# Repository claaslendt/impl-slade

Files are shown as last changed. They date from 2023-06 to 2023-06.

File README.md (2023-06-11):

Author: Claas Lendt (I'm tweeting @claaslendt)

Last modified: 10.06.2023

*Note: This is a living documentation and will be continuously extended and reviewed.*

</br>

## A wearable system to estimate energy expenditure

My PhD research focusses on the development and validation of new computational methods to monitor human physical behaviour based on the acceleration of the thigh. One key area of my research is the estimation of activity-induced energy expenditure. In other words, I want to develop an accurate algorithm to estimate how many calories are burned when someone is physically active. To achieve this goal, I need data to develop my algorithm and see how accurate it really is. These data include a primary reference for the energy expenditure (also considered ground truth), raw triaxial acceleration of the thigh and further references from existing methods.

One particular method I want to compare my algorithm against is the wearable system proposed by Patrick Slade and colleagues (Link to the paper: [Slade et al. 2021 - Nature Communications](https://www.nature.com/articles/s41467-021-24173-x)). It comprises two inertial measurement units (IMUs) on the thigh and the shank, a Raspberry Pi as the computing unit, a rechargeable battery and a regression model. The estimation of the energy expenditure is based on a linear regression model with accelerometer and gyroscope data as inputs. Their novel approach uses stride segmentation of the IMU data and then performing the energy expenditure estimation on discrete stride cycles. This is super interesting, given that most other computational methods are based on some form of regression model with an aggregated measure of the acceleration over a fixed time interval. Overall, a highly innovative and quite accurate approach!

It seems like the wearable system from Patrick Slade et al. is a good candidate to compare my future estimations against! So I decided to recreate the system based on the information given in the paper and its supplementary documents. It's been quite a journey, given that I had almost zero knowledge on the Raspberry Pi, I2C addresses or 3D printing at the start of this project.

</br>

## Building the system (almost) from scratch

To start with, I chose a [Raspberry Pi Zero 2 W](https://www.raspberrypi.com/products/raspberry-pi-zero-2-w/) as my computing unit. It's quite compact compared to the Raspberry Pi 4 and still powerful enough to allow the collection and processing of the IMU data. Further, it can easily run Python code. I haven't used any Raspberry Pi before, but it was extremely easy to get started. There are great documentations available online (see [raspberrypi.com/documentation](https://www.raspberrypi.com/documentation/computers/getting-started.html)) and setting up the mini-computer can be done in short time.

As for the IMUs, I chose the [Adafruit ISM330DHCX](https://www.adafruit.com/product/4502) sensor breakout boards. These sensors allow to capture a range of ±16 g of acceleration and up to ±4000 dps. The breakout boards are great because they can easily be connected to a computing unit using the integrated STEMMA QT connectors. In my case, the Raspberry Pi and the IMUs are connected using 50cm [STEMMA QT](https://www.adafruit.com/product/5385) (also called "Qwiic") connection cables and a [SparkFun Qwiic SHIM adapter](https://www.adafruit.com/product/4463) for the Raspberry Pi. At the beginning, I thought I could create the system without the need for any soldering. But I was wrong. Thankfully, I got support from our electronics lab in soldering the pins to the Raspberry Pi and the adapter as well as setting the alternative I2C address for the IMU at the shank.

The final component is an 10.000mAh USB rechargeable battery to power the system during mobile use. The battery is simply connected to the Raspberry Pi using a short USB cable (USB-A to micro-USB). I went with the Ansmann PB320PD.

</br>

**Figure 1.** The Raspberry Pi Zero 2 W, the two Adafruit IMUs and the STEMMA QT/Qwiic connections using the SparkFun SHIM adapter on the Raspberry Pi.

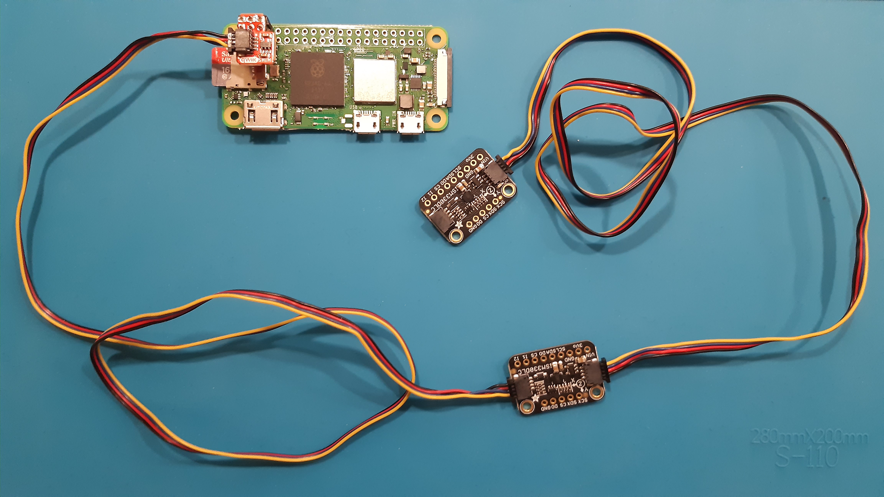
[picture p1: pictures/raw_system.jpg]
raw_system


</br>

### 3D printing the cases

The two IMUs and the Raspberry Pi need to be attached to the body and be protected from receiving any damage during movements. I decided to 3D print my own cases since there wasn't any simple solution available. My starting point was the great article [3D Printed Case for Adafruit Feather](https://learn.adafruit.com/3d-printed-case-for-adafruit-feather/3d-printing) and I iteratively developed my own version to fit the Raspberry Pi Zero and a smaller case for the IMUs. I used Autodesk Fusion 360 for the modelling of the individual parts, which required some time to learn the software. A much easier and no-cost option may be [Autodesk's Tinkercad](https://www.tinkercad.com/).

Each case consists of a base unit and a top. The connection cables can be attached through the small holes. The Raspberry Pi and the IMU boards are attached to the case using small plastic screws (M2.5) and hex nuts. I am also sharing the files used for printing within the 3d_printing folder.

</br>

**Figure 2.** The two cases for the IMUs with the screws and hex nuts fixating the IMUs to the case. The additional wings on the cases are used to attach the cases with additional elastic straps (see below).

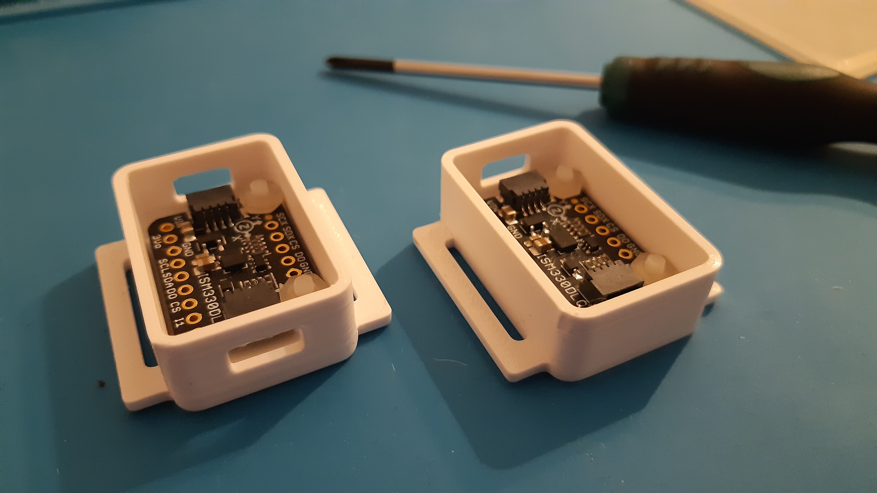
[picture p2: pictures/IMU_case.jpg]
IMU_case


</br>

### Attaching the IMUs to the leg

I did quite some experimenting with different elastic straps to attach the sensors to the thigh and shank as I wanted them to be lightweight, comfortable and not slipping too much. At the end, I found some elastic straps which are used to attach urine drainage bags (see [MedlinePlus: Medical Encyclopaedia](https://medlineplus.gov/ency/patientinstructions/000142.htm)) and they work great! The strap has a layer of silicone rubber which prevents any slippage during movements of the leg and can easily be attached using the velcro. The PZN (German Medical Product ID) for these particular straps is 08913533.

</br>

**Figure 3.** The medical straps used to attach the sensor units to the shank and thigh.

elastic_strap

</br>

## The final system - completed!

When everything is put together, the Raspberry Pi and the battery are attached to the waist using an elastic belt with a quick-release. The two IMUs are attached to the shank and thigh. The system has been quite comfortable during my piloting (walking and running on a treadmill as well as cycling on an ergometer).

</br>

**Figure 4.** The left (A) shows the complete system with the battery (lower left) connected to the Raspberry Pi (lower right) via USB. The Raspberry Pi is connected to the IMU at the thigh via Qwiic cable. Finally, the two IMUs are connected using another Qwiic cable. The system is attached to the left leg (B).

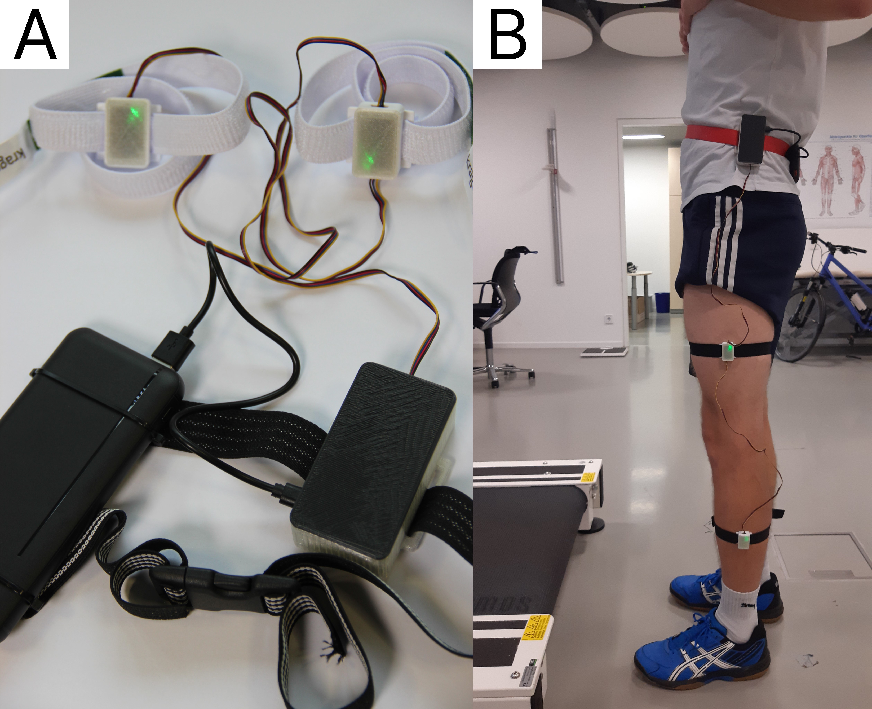
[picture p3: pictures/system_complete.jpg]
system_complete


</br>

## Software and the modelling approach

Patrick Slade is openly sharing the Python code to run his model on GitHub / Zenodo (DOI: [10.5281/zenodo.4891703](https://doi.org/10.5281/zenodo.4891703)). It only requires a single code file and the model weights, which are stored within a .csv file. The two files can easily be transferred on the Raspberry Pi and run using the preinstalled Thonny Python IDE.

There is a great tutorial using [Google Colab: Tutorial - Estimating Energy Expenditure](https://colab.research.google.com/github/stanfordnmbl/mobilize-tutorials/blob/main/Tutorial_Estimating_Energy_Expenditure_During_Exercise.ipynb#scrollTo=iRwsQrItNHaX) and a webinar by Patrick Slade ([Stanford mobilize - Webinar: Estimating Energy Expenditure During Exercise Using Wearable Sensors](https://mobilize.stanford.edu/webinar-estimating-energy-expenditure-during-exercise-using-wearable-sensors/)). I can highly recommend both resources to further understand the system and modelling approach. **Thanks to Patrick for putting all these great resources out there and making the model open-source!** :rocket:

</br>

### Acknowledgements

I want to thank Thomas Förster for supporting me with the soldering, the [MakerSpace Bonn](https://makerspacebonn.de/) for providing me with all the knowledge and tools for 3D printing and Theresa Braun for the overall support.

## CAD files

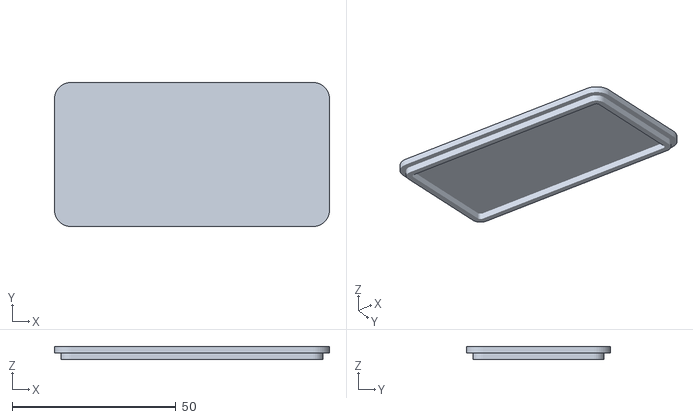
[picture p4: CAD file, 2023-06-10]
3d_printing/PiZero_top.stl
84.0 x 44.0 x 4.00

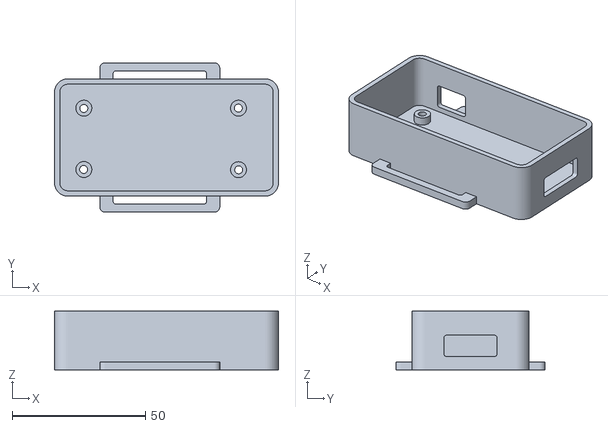
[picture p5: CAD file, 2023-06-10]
3d_printing/PiZero_case.stl
84.0 x 56.0 x 22.0

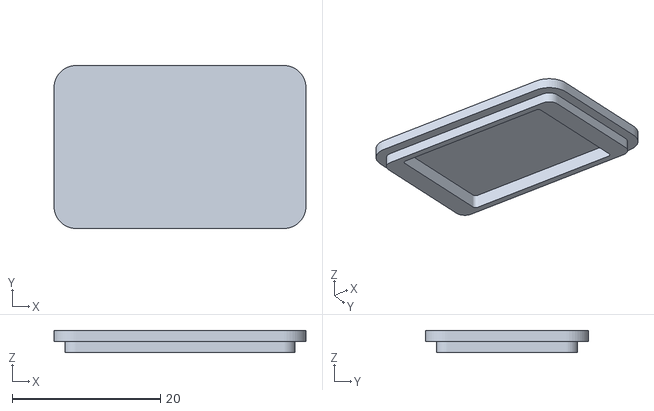
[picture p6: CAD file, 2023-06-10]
3d_printing/IMU_top.stl
34.0 x 22.0 x 3.00

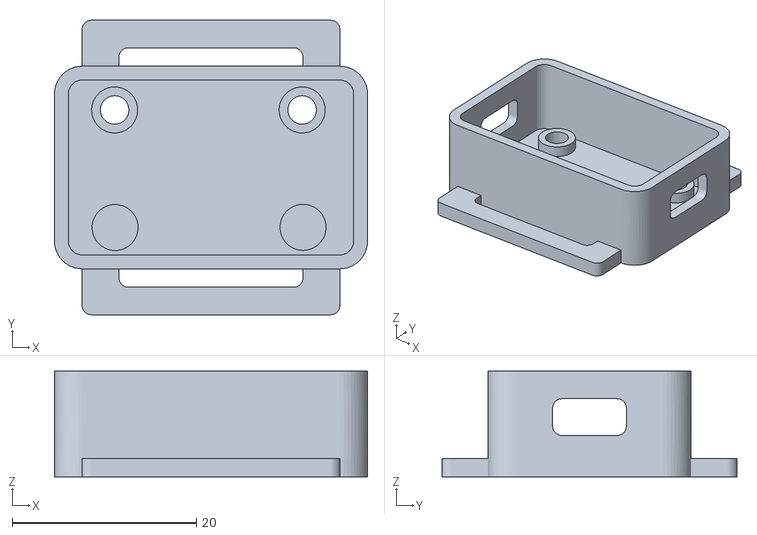
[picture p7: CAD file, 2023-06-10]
3d_printing/IMU_case_thigh.stl
34.0 x 32.0 x 11.5

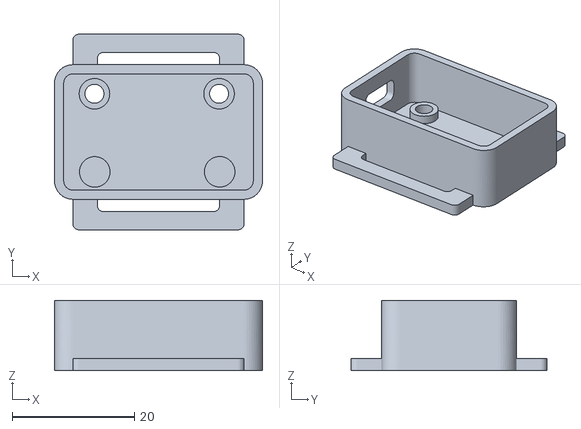
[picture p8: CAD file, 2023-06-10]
3d_printing/IMU_case_shank.stl
34.0 x 32.0 x 11.5
